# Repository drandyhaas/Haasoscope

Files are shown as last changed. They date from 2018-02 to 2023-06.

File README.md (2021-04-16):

# Haasoscope

Docs, design, firmware, and software for the Haasoscope!
Read the guide here: https://goo.gl/1Ry1k4 

Original funding campaign: https://www.crowdsupply.com/andy-haas/haasoscope (see the "updates" tab for lots of info)
Now also for sale on eBay - just search for "Haasoscope": https://www.ebay.com/sch/i.html?_nkw=haasoscope

A changelog for the python code is here: https://docs.google.com/document/d/18tjrI03KipmFqbNIHOzAKYy1VVE9wWbefSHazbPP8Gc/edit?usp=sharing and it also has pointers to changelogs for the firmware, board, and android app.

3D printable cases are available (see the guide for info)

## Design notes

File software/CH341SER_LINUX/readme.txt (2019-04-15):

// ChangeLog 
// 1.0 - 1.1   modified to solve transmition between ch341 and ch341
// 1.1 - 1.2   Support high Linux kernel
Instructions

Note: 1.Please run followed executable programs as root privilege
      2.Current Driver support versions of linux kernel range from 2.6.25 to 3.13.x
      3.Current Driver support 32bits and 64bits linux systems

Usage:
	(load or unload linux driver of CH34x)
	//compile 
	#make
	//load ch34x chips driver
	#make load
	//unload ch34x chips driver
	#make unload

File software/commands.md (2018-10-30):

Commands are received in [serialprocessor.v](../max10_adc_firmware/serialprocessor.v) and handled [in the SOLVING case](../max10_adc_firmware/serialprocessor.v#L253). Each command has a starting `id` number. Some commands take additional arguments. Commands are passed along a multiboard chain so they are seen by all boards.

`0-9` tells the board its `ID`. The first board will get usually be sent a `0`, and then it sends a `1` to the next board, which then sends a `2` to the next, and so on. Board `0` is special since it creates the clock for all boards.

`10-19` tells the board with ID 10 less to send its event data. For instance, `10` will tell board `0` to send its data. The data will be 4 channels of fast ADC data, plus additional info if other options are enabled. Each channel is sent in order, starting with channel `0`. N samples are sent for each channel, from earliest to latest in time. Each sample is one byte (8 bits), where `0` is the highest voltage for the input (e.g. 3.75V), and `255` is the lowest (e.g. -3.75V). (It's an inverting op-amp configuration.)

`20-29` tells the board with ID 20 less that it's the last one (the highest ID). For instance, sending 21 tells board with `ID 1` that it's the last board. It needs to know this in order to ignore signals on its unconnected trigger inputs on its left-side male connector.

`30-39` tells the board with ID 30 less to be the "active" board. For instance, `31` would tell the board with `ID 1` to be active, and all other boards to the right of it to be in "passthrough". Then sending another request for some data with come from the active board, and be passed through the boards to its right. If one wanted to get the board unique max10 string from board `2`, they would send `32` followed by the command to send the unique string (142).

`100` tells all boards to "arm" their triggers, and then record a new event. Note that there is also an auto-rearm mode which will always get a new event after sending the last one (see below). If the board does not record a new event, it will continue to send the same event each time it is asked to send an event.

`101`/`102` tells boards to roll / not roll the trigger. Rolling the trigger means automatically generating a trigger every 0.2 seconds (like auto mode on a scope).

`110-119` tells boards to send the "slow ADC" data from a given pin. For instance, 110 sends the data from all boards from slow ADC input 1 (pin 6), 118 would send slow ADC data from input 8 (pin 14), etc. The data is sent as N samples (set below), and each sample is 2 bytes. The first byte is the lowest 8 bits (0-255), and the second holds the higher 4 bits (0-15). It's a 12-bit ADC. So the 12-bit value is 256 times the second byte plus the first byte.

`120` (+ 2 more bytes) is how many slow ADC samples to send. It is `256*a+b` samples, where `a` is the first byte and `b` is the second byte. For instance, `120 1 10` would send `256*1+10=266` samples.

`121` (+ 2 more bytes) is the trigger point in time (how many samples to record before the trigger). It is `256*a+b` samples, where `a` is the first byte and `b` is the second byte. Add pow(2,12) to the number (i.e. 16 to a) in order to use the current timebase in the calculation (recommended!).

`122` (+ 2 more bytes) is how many fast ADC samples to send. It is `256*a+b` samples, where `a` is the first byte and `b` is the second byte. For instance, `122 1 100` would send `256*1+100=356` samples.

`123` (+ 1 more byte) is how many fast ADC samples to skip sending after each sample sent. The byte is `2^n`, e.g. if the byte is `3`, then `2^3=8` samples are skipped.

`124` (+ 1 more byte) is the "timebase", i.e. what fraction of fast ADC samples to actually record. It is `1/2^n`, so if the byte is `3`, then `1/2^3=1/8` fast ADC samples are recorded.

`125` (+ 1 more byte) is the number of clock ticks (20ns) to wait between sending serial bytes. It is `2^n`, so if the byte is `4`, then `2^4=16` ticks are waited.

`126` (+ 1 more byte) is the channel to draw on the miniscreen, e.g. `126 3` would draw channel 3 on each board's mini-screen.

`127` (+ 1 more byte) sets the trigger threshold for the fast ADC channels.

`128` (+ 1 more byte) is the type. If the byte is `1` it's a rising edge, if it's `0` it's falling.

`129` (+ 2 more bytes) is how long a channel must be above/below the trigger threshold to fire it. It is `256*a+b samples`, where a is the first byte and b is the second byte.

`130` (+ 1 more byte) toggles whether the trigger is active for a given channel, e.g. `130 6` would toggle the trigger activity for channel 6.

`131` (+ 2 more bytes) is for talking to the SPI interface on the fast ADCs on all boards. The first byte is the 7 bit address to send to on the ADC, and the second is the byte sent to that address. See the [max19506 datasheet](https://datasheets.maximintegrated.com/en/ds/MAX19506.pdf) for info, and/or see [example commands in the python programs](https://github.com/drandyhaas/Haasoscope/blob/master/software/HaasoscopeLib.py#L250).

`132/133` will send the delaycounter / carrycounter extra data (1 byte) from the active board.

`134` (+ 1 more byte) toggles the x10 gain for a given channel, e.g. `134 6` would toggle the x10 gain for channel 6.

`135` (+ 2 more bytes) says how many 2us ticks to wait after sending each 32 bytes of serial data (serialdelaytimerwait). It is `256*a+b` ticks, where a is the first byte and b is the second byte.

`136` (+ 6 more bytes!) talks over i2c to the IO expanders and DAC on the boards. The first bytes is how many bytes of info to send (not counting address). The second byte is the i2c address to send to. The 3rd-5th bytes are the data to send. And the 6th byte is which board ID to talk to (or 200 to talk to all boards). [See the python programs for examples of commands](https://github.com/drandyhaas/Haasoscope/blob/master/software/HaasoscopeLib.py#L299).

`137` toggles whether data is sent back over the serial interface or the USB2 hat.

`138` is how many ADC samples to shift the reference wave by in order to be 90deg out of phase, for lockin calculations in the FPGA.

`139` toggles auto-rearming of the trigger. Without it, you need to send `100` to record a new event each time.

`140` (+ 1 more byte) sets the "runt" trigger threshold for the fast ADC channels.

`141` (+ 1 more byte) toggles the oversampling for a given channel, e.g. `130 4` would toggle oversampling for channel 4.

`142` tells the active board to send its unique 8-byte ID back over serial.

`143` toggles "high-res" mode for all channels.

`144` toggles whether the external trigger pin is active, for all boards.

-- Following commands require the [new firmware](../max10_adc_firmware/output_files)!

`145` (+ 1 more byte) is how many channels to send data for, from each board. For instance, `145 4` would send all 4 channels from all boards. Note that the logic analyzer data is the "5th channel" on each board, so `145 5` sends all 4 channels plus the logic analyzer data. The logic analyzer data is the same number of samples as and synchronous with the fast ADC data. It is 1 byte per sample, and each bit is 0/1 for each of the 8 logic analyzer pins being low/high.

`146` (+ 3 more bytes) requests a byte to be read from i2c (e.g. ioexpander inputs) from a given i2c address, chip address, and board.

`147` requests the firmware version byte to be sent back over serial from the currently active board.

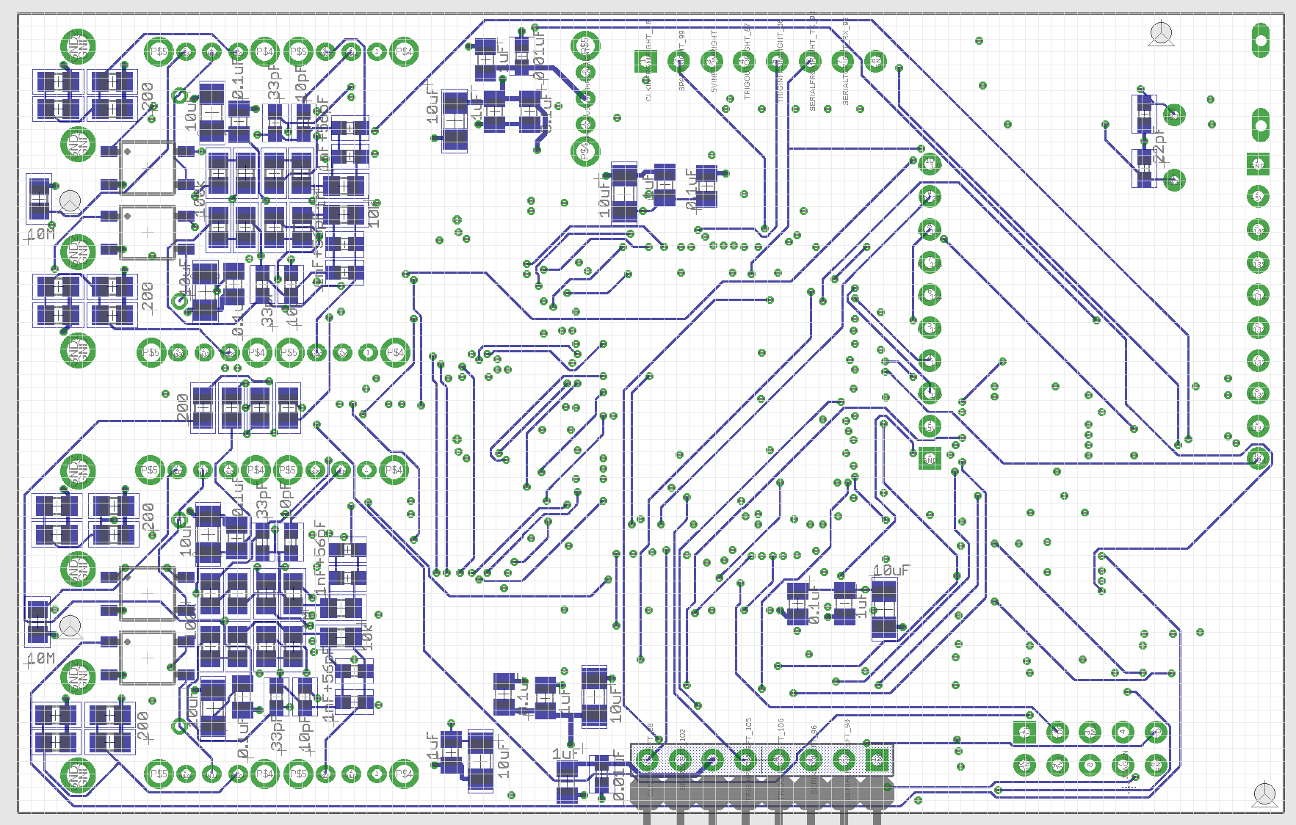
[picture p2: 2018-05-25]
eagle/max10adc_bottom_v8.png

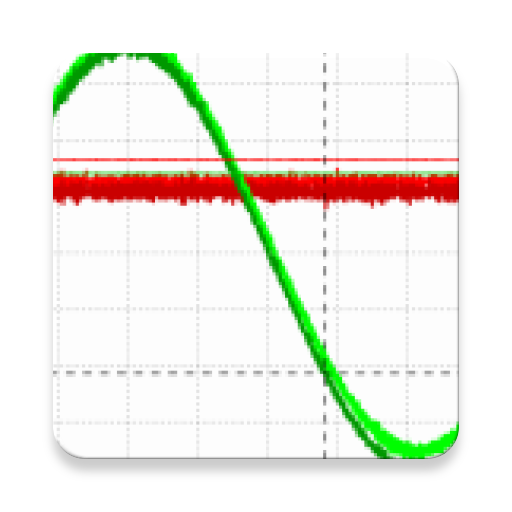
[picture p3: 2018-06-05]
android/example/src/main/ic_launcher-web.png

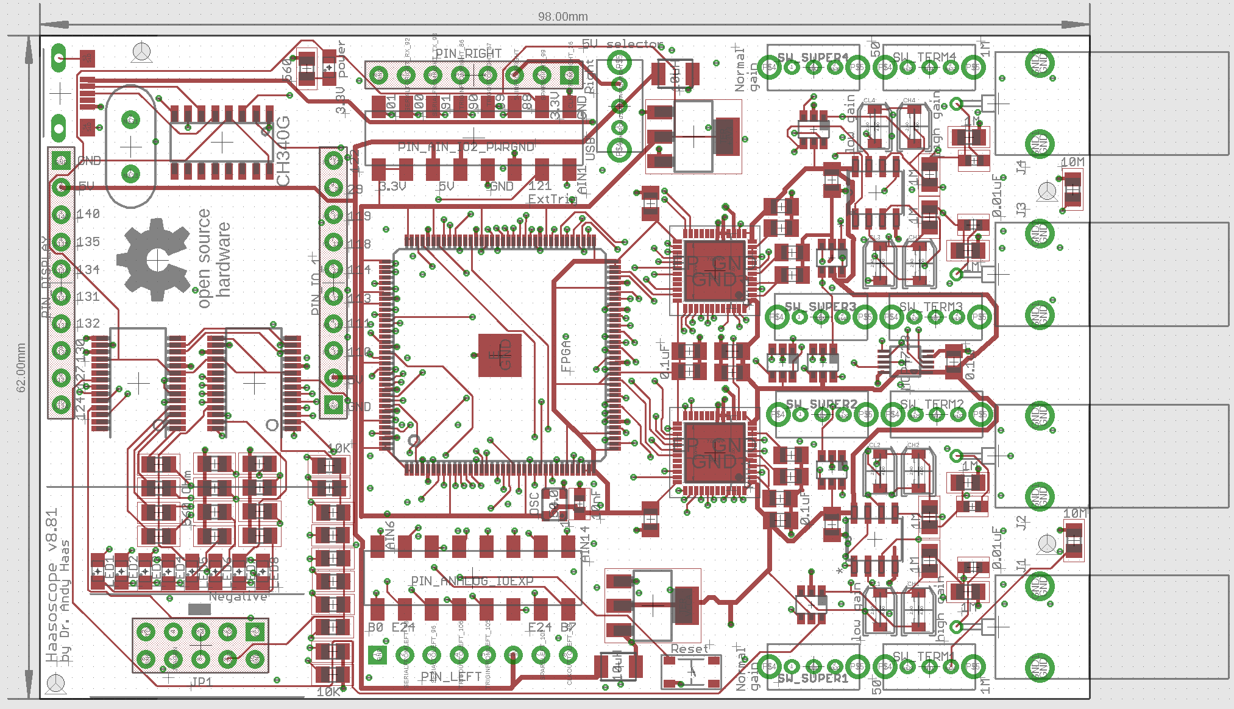
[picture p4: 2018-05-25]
eagle/max10adc_top_v8.png

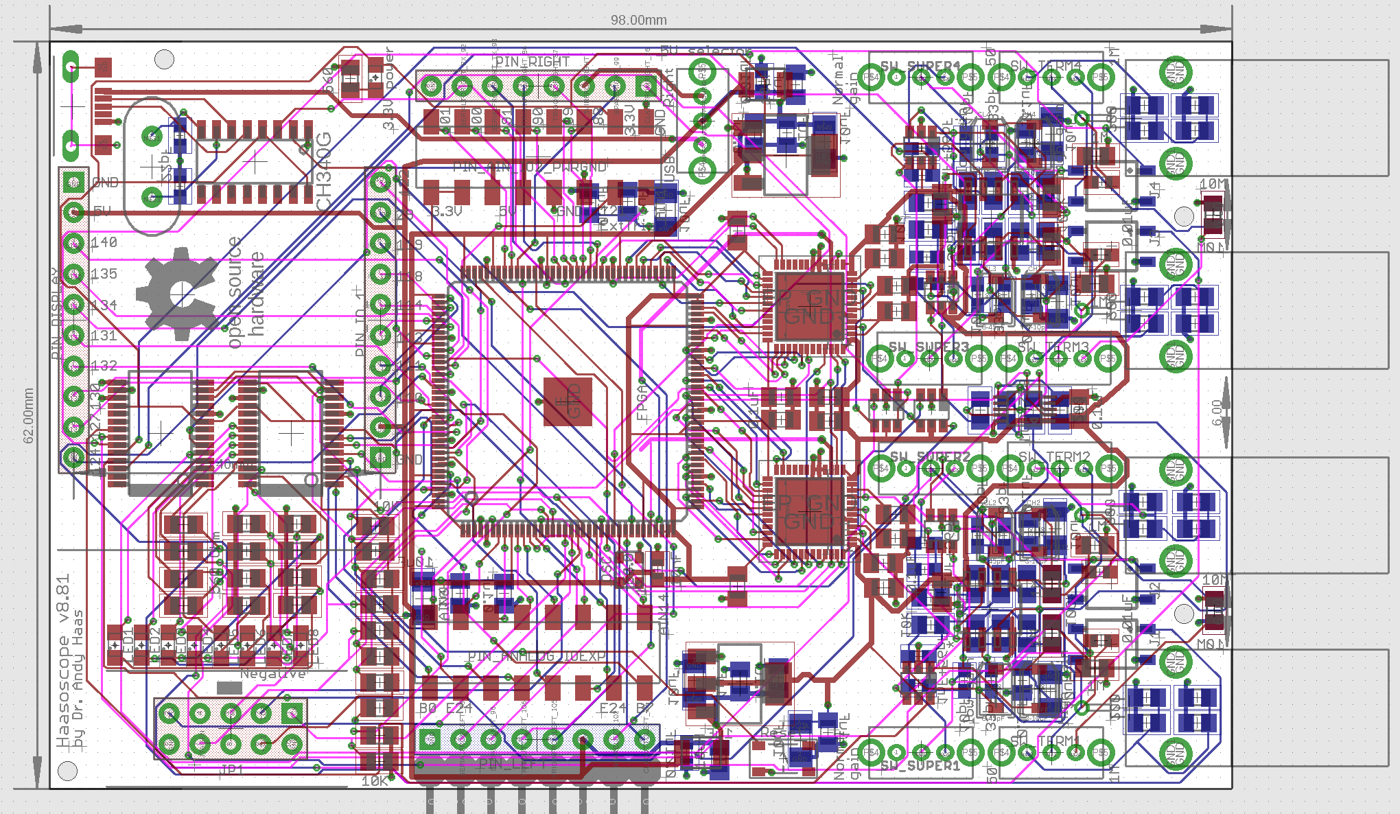
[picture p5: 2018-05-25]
eagle/max10adc_v8.png

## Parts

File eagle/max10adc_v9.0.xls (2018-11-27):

Qty | Value | Device | Package | Parts | Description | MPN | SMD | Price $ (in QTY 250 boards) | Price total (in QTY 250 boards) | Link
1 | 10M08SAE144 | 10M08SAE144 | EQFP144 | FPGA | FPGA | 10M08SAE144C8G | Yes | $16.99 | $16.99 | https://octopart.com/search?q=10M08SAE144C8G&start=0
2 | MAX19506 | MAX19506 | TQFP-48 | IC1, IC2 | analog-to-digital converter | MAX19506ETM+ | Yes | $6.77 | $13.54 | https://www.mouser.com/ProductDetail/Maxim-Integrated/MAX19506ETM%2b?qs=sGAEpiMZZMvTvDTV69d2QhUo9pNzAfXNT3AANbfnPJ4%3d
2 | MAX4416ESA | MAX4416ESA | M08A | U1, U2 | op amp | MAX4416ESA | Yes | $2.29 | $4.58 | https://www.mouser.com/ProductDetail/Maxim-Integrated/MAX4416ESA%2b?qs=sGAEpiMZZMsko7UDAsUSIQKhiCsYDWs9zfYsCt0hbUU%3d
4 | AQY21SOP | AQY21SOP | SOP04 | K1, K2, K3, K4 | PhotoMOS Relay NAiS | AQY210SZ | Yes | $0.97 | $3.86 | https://octopart.com/search?q=AQY210SZ&start=0
9 | JS202011SCQN | JS202011SCQN | JS202011SCQN | S1, S2, S3, S4, S5, S6, S7, S8, S9 | DPDT Switch | JS202011SCQN | Yes | $0.25 | $2.29 | https://octopart.com/search?q=JS202011SCQN&start=0
4 | MOLEX_BNC_73100-0105 | MOLEX_BNC_73100-0105 | MOLEX-BNC-73100-0105 | J1, J2, J3, J4 | CONN BNC JACK R/A 50 OHM PCB | 73100-0105 | No | $0.57 | $2.28 | https://www.ttiinc.com/content/ttiinc/en/apps/part-detail.html?partsNumber=73100-0105&mfgShortname=MOL&utm=tti-octo&channel=ppc&campaigns=tti-brand
2 | MCP23017SS | MCP23017SS | SSOP28 | IOEXPAND_0X20_BOT, IOEXPAND_0X24_TOP | IO expander | MCP23017-E/SS | Yes | $0.90 | $1.80 | https://octopart.com/search?q=MCP23017-E%2FSS&start=0
1 | MCP4728 | MCP4728 | MSOP10 | DAC1 | DAC | MCP4728-E/UN | Yes | $1.40 | $1.40 | https://octopart.com/search?q=MCP4728-E%2FUN&start=0
4 | 8-45pF | CAP_ADJSMD | CTZ3 | CL1, CL2, CL3, CL4 | Variable, non-polarized capacitor | TZY2K450AC01 | Yes | $0.33 | $1.31 | https://octopart.com/search?q=TZY2K450AC01&start=0
1 | ASE-50.000MHZ-ET | ASE | ASE | OSC | 3.3V CMOS SMD OSCILLATOR | ASE-50.000MHZ-ET | Yes | $1.23 | $1.23 | https://octopart.com/search?q=ASE-50.000MHZ-ET&start=0
4 | 3-10pF | CAP_ADJSMD | CTZ3 | CH1, CH2, CH3, CH4 | Variable, non-polarized capacitor | TZY2Z100AC01 | Yes | $0.25 | $0.98 | https://octopart.com/search?q=TZY2Z100AC01&start=0
2 | 15-91-2160 | PINHD-2X8SMT | 2X08_SMT | PIN_AIN_IO2_PWRGND, PIN_ANALOG_IOEXP | PIN HEADER | 15-91-2160 | Yes | $0.48 | $0.97 | https://www.ttiinc.com/content/ttiinc/en/apps/part-detail.html?partsNumber=15-91-2160&mfgShortname=MOL&utm=tti-octo&channel=ppc&campaigns=tti-brand
9 | 10uF | C-USC1206 | C1206 | CG14, COFFSETA1, COFFSETA2, COFFSETA3, COFFSETA6, CP3, CP4, CP5, CP6 | CAPACITOR, American symbol | MF-CAP-1206-10uF | Yes | $0.08 | $0.71 | https://octopart.com/search?q=C3216X5R1C106M160AA&start=0
6 | 741G3157DBVR | 741G3157DBVR | DBV_R-PDSO-G6 | GAINSW1, GAINSW2, GAINSW3, GAINSW4, OVSAMP1, OVSAMP2 | Single-Pole, Double-Throw Analog Switch | SN74LVC1G3157DBV | Yes | $0.09 | $0.55 | https://octopart.com/search?q=SN74LVC1G3157DBV&start=0
2 | LDL1117S33R | PMIC-CJT1117-3.3(SOT223) | SOT-223 | REG, REG1 | LDO regulator | LDL1117S33R | Yes | $0.18 | $0.36 | https://octopart.com/search?q=LDL1117S33R&start=0
1 | CH340G | CH340G | SOIC16 | U340G | Usb serial chip | CH340G | Yes | $0.36 | $0.36 | https://www.ebay.com/itm/50PCS-CH340G-CH340-SOP-16-IC-new-/291548393770
5 | MF-LED-0805-RED | LEDSML0805 | SML0805 | LED1, LED2, LED3, LED4, LEDPOW | LED | MF-LED-0805-RED | Yes | $0.06 | $0.32 | https://octopart.com/search?q=LTST-C171CKT&start=0
1 | MF-CON-MICROUSB-RIGHT | USB_5PIN_10118193-0001LF | 10118193-0001LF | USB1 | USB connector | MF-CON-MICROUSB-RIGHT | No | $0.29 | $0.29 | https://octopart.com/search?q=10118193-0001LF&start=0
1 | MF-SW-TACT-4.2MM | TACT_4.2MM | TACT4.2MM | SW_RESET | Reset momentary switch | MF-SW-TACT-4.2MM | Yes | $0.25 | $0.25 | https://octopart.com/search?q=PTS810%20SJK%20250%20SMTR%20LFS&start=0
25 | 0.1uF | C-EUC0805K | C0805K | C-AIN1, C-AIN2, C-AIN3, C-AIN4, C0DD1_A, C0DD2_A, C0DD2_B, C5VOPAMP1, C5VOPAMP2, CADD1_A, CADD1_B, CADD2_A, CADD2_B, CG15, CODD1_B, COFFSET, COFFSETB6, COFFSETB8, COFFSETB10, COFFSETB12, CP2, CP8, CREF1, CREF2, CV11 | CAPACITOR, European symbol | MF-CAP-0805-0.1uF | Yes | $0.01 | $0.25
1 | ABL-12.000MHZ-B2 | CRYSTALHC49US | HC49US | Y1 | Usb serial oscillator | ABL-12.000MHZ-B2 | No | $0.23 | $0.23 | https://octopart.com/search?q=ABL-12.000MHZ-B2&start=0
2 | 10uH | INDUCTOR1210 | 1210 | L1, L2 | Inductors | MF-IND-1210-10uH | Yes | $0.10 | $0.21 | https://octopart.com/search?q=LBC3225T100KR&start=0
20 | 200 | R-US_R0805 | R0805 | R50-1, R50-2, R50-3, R50-4, R50-5, R50-6, R50-7, R50-8, R50-9, R50-10, R50-11, R50-12, R50-13, R50-14, R50-15, R50-16, ROFFSET1, ROFFSET2, ROFFSET3, ROFFSET4 | RESISTOR, American symbol | MF-RES-0805-200 | Yes | $0.01 | $0.20
1 | 8p-2.54-90d | DIP-BLACK-FEMALE-HEADER-R/A(8P-2.54-90D) | H8-2.54-90D-FEMALE | PIN_RIGHT | Right side right-angle female connector | 8p-2.54-90d | No | $0.17 | $0.17 | https://www.ebay.com/itm/20PCS-2-54mm-1x8Pin-Pitch-Header-Right-Angle-Female-Single-Row-Socket-Connector/172194742559
4 | 56pF | C-USC0603 | C0603 | CIN56_1, CIN56_2, CIN56_3, CIN56_4 | CAPACITOR, American symbol | 06035A560FAT2A | Yes | $0.04 | $0.17 | https://octopart.com/search?q=06035A560FAT2A&start=0
2 | YELLOW-10P-2.54 | DIP-YELLOW-FEMALE-HEADER-VERT(10P-2.54) | H10-2.54 | PIN_DISPLAY, PIN_IO_1 | 1x10 header | YELLOW-10P-2.54 | No | $0.07 | $0.14 | https://www.ebay.com/itm/100PCS-2-54mm-1x10-Single-Row-10-Pins-Header-PCB-Socket-Female/182121619399
4 | 1nF | C-USC0603 | C0603 | CIN1NF_1, CIN1NF_2, CIN1NF_3, CIN1NF_4 | CAPACITOR, American symbol | 06035A102JAT2A | Yes | $0.03 | $0.11 | https://octopart.com/search?q=06035A102JAT2A&start=0
4 | 10M | R-EU_R0805 | R0805 | RIN5, RIN6, RIN7, RIN8 | RESISTOR, European symbol | CRCW080510M0FKEB | Yes | $0.03 | $0.10 | https://octopart.com/search?q=CRCW080510M0FKEB&start=0
1 | 2x5p-2.54 | DIP-BLACK-MALE-HEADER(2X5P-2.54) | H2X5-2.54 | JP1 | JTAG connector | 2x5p-2.54 | No | $0.10 | $0.10 | https://www.ebay.com/itm/100Pcs-Dual-Row-5-X-2-Isp-Download-Jtag-I-O-Socket-DC3-10P-2-54MM-Pitch-New-I-rn/223137742292
9 | 560 | R-EU_R0805 | R0805 | ACR1, ACR2, ACR3, ACR4, RLED1, RLED2, RLED3, RLED4, RLEDPOW | RESISTOR, European symbol | MF-RES-0805-560 | Yes | $0.01 | $0.09
8 | 100k | R-EU_R0805 | R0805 | RGAIN1_1, RGAIN1_2, RGAIN1_3, RGAIN1_4, RGAIN3_1, RGAIN3_2, RGAIN3_3, RGAIN3_4 | RESISTOR, European symbol | MF-RES-0805-100k | Yes | $0.01 | $0.08
8 | 1M | R-EU_R0805 | R0805 | RGAIN2_1, RGAIN2_2, RGAIN2_3, RGAIN2_4, RGAIN4_1, RGAIN4_2, RGAIN4_3, RGAIN4_4 | RESISTOR, European symbol | MF-RES-0805-1M | Yes | $0.01 | $0.08
8 | 10K | R-EU_R0805 | R0805 | RJ2, RJ3, RJ4, RJ5, RS6, RS7, RS8, RS9 | RESISTOR, European symbol | MF-RES-0805-10K | Yes | $0.01 | $0.08
4 | 33pF | C-USC0603 | C0603 | CGAIN1_1, CGAIN1_2, CGAIN1_3, CGAIN1_4 | CAPACITOR, American symbol | 06033A330JAT2A | Yes | $0.02 | $0.08 | https://octopart.com/search?q=06033A330JAT2A&start=0
7 | 0.01uF | C-USC0603 | C0603 | C_5V_10NF, C_5V_10NF1, C_AC1, C_AC2, C_AC3, C_AC4, C_OSC | CAPACITOR, American symbol | MF-CAP-0603-0.01uF | Yes | $0.01 | $0.07
7 | 1uF | C-EUC0805K | C0805K | CG13, CP1, CP7, CP9, CP10, CP11, CV12 | CAPACITOR, European symbol | MF-CAP-0805-1uF | Yes | $0.01 | $0.07
4 | 1.1M | R-EU_R0805 | R0805 | RIN1, RIN2, RIN3, RIN4 | RESISTOR, European symbol | CRCW08051M10FKEA | Yes | $0.01 | $0.05 | https://octopart.com/search?q=CRCW08051M10FKEA&start=0
4 | 11K | R-EU_R0805 | R0805 | RIN1_11K, RIN2_11K, RIN3_11K, RIN4_11K | RESISTOR, European symbol | CRCW080511K0FKEA | Yes | $0.01 | $0.04 | https://octopart.com/search?q=CRCW080511K0FKEA&start=0
4 | 10pF | C-USC0603 | C0603 | CIN5_1, CIN5_2, CIN5_3, CIN5_4 | CAPACITOR, American symbol | MF-CAP-0603-10pF | Yes | $0.01 | $0.04
2 | 22pF | C-USC0603 | C0603 | C_OSC1, C_OSC2 | CAPACITOR, American symbol | MF-CAP-0603-22pF | Yes | $0.01 | $0.02
2 | 10K | R-EU_R0805 | R0805 | R_SCL, R_SDA | RESISTOR, European symbol | MF-RES-0805-10K | Yes | $0.01 | $0.02
1 | 8p-2.54-90d | DIP-BLACK-SHORT-MALE-HEADER-R/A(8P-2.54-90D) | H8-2.54-90D-MALE | PIN_LEFT | Left side right-angle male connector | 8p-2.54-90d | No | $0.02 | $0.02 | https://www.ebay.com/itm/12Pcs-2-54mm-Pitch-Single-Row-Male-90-Degree-Right-Angle-Pin-Header-Q7Y4/253139448716
193 |  |  |  |  |  |  |  |  | $56.50 | Total parts
 |  |  |  |  |  |  |  |  | $9.75 | Total minor parts

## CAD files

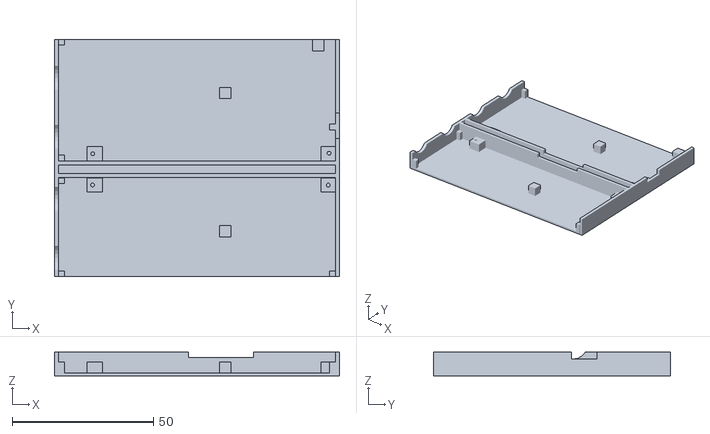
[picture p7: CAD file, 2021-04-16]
3d/Haasoscope_v9.01_case_connect.stl
101.0 x 84.0 x 8.50

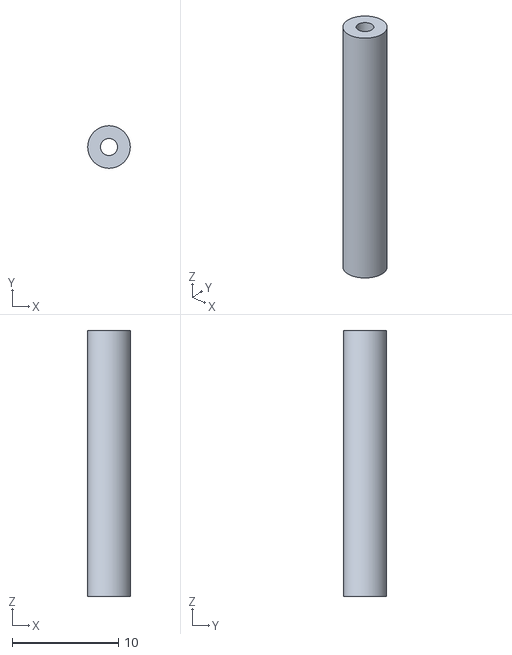
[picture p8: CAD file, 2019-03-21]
3d/customizable-cylinder_25mm.stl
4.00 x 4.00 x 25.0

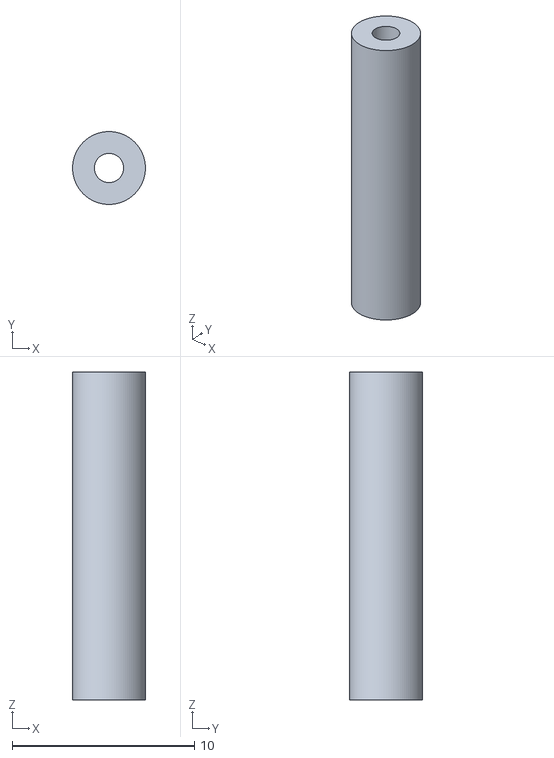
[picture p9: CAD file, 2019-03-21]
3d/customizable-cylinder_18mm.stl
4.00 x 4.00 x 18.0

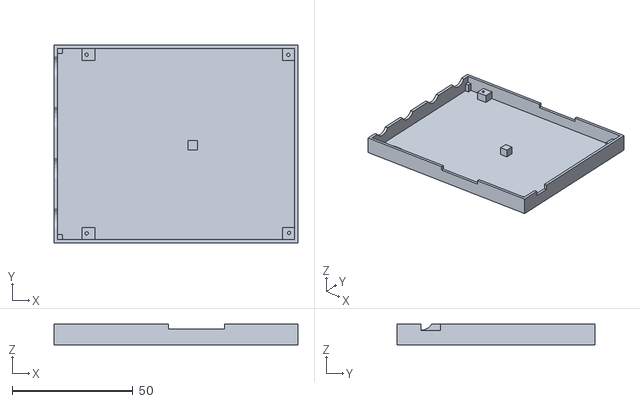
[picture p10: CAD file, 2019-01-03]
3d/Haasoscope_v9.01_case.stl
101.0 x 82.0 x 8.50

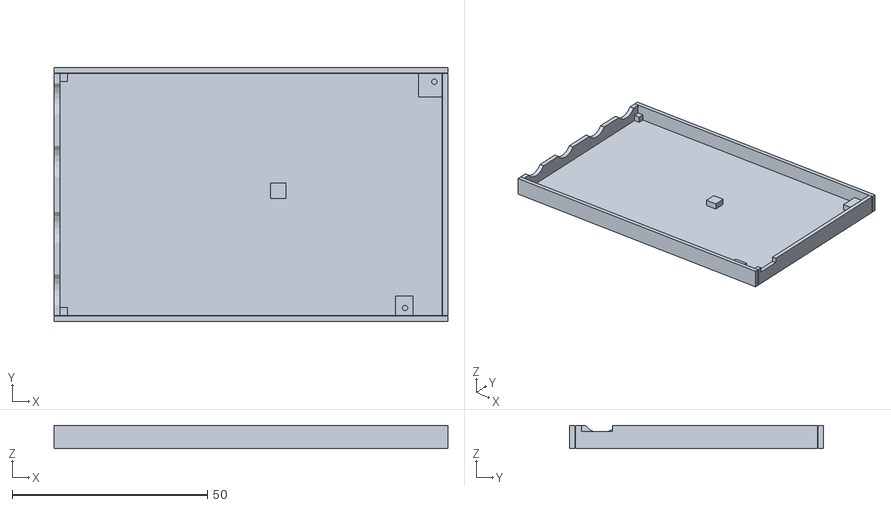
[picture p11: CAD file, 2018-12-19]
3d/Haasoscope_v8.81_case.stl
101.0 x 65.0 x 6.00

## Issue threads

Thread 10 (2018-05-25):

drandyhaas/Haasoscope #10: Probes won't compensate

g8sqh, 2018-05-25:
Cut down the probe trim tool and adjusted the pcb trimmers to get nice square waves

The probes supplied won't compensate. This is fixable thus:
- Pull the cable strain relief away from the BNC plug, and slide off the small 'box' cover
- Next to the black trimmer on the probe PCB solder on a 120 (one hundred and twenty) pF capacitor onto the two empty pads
- Refit the cover and the strain relief

This done the probes will also compensate (normal gain on PCB).

Thanks for a great product

drandyhaas, 2018-05-25:
This is true. And thanks for the tip/fix!
To be clear for others, the probe compensation (screw on the probe itself) only affects the 10x probe setting (switch on the probe itself). 
Also, the lack of compensation only affects signals below ~50 kHz, which is why I never worried too much about it. I think the reason it fails to compensate with the default cap in the probe is that I have too much (or too little?) capacitance at the BNC input. (?)

g8sqh, 2018-05-25:
I don't understand the value I needed. A normal 'real' old-fashioned scope was a fixed 30pF in parallel with 1M - they actually had trimmers on the input attenuator to keep the value constant (as well as another trimmer for compensation)

Later scopes went down to 20pF, and I think a few reached 14pF - always to reduce the loading on the circuit being measured. The screw in the probe box is directly across the BNC connector - and thus corrects for the 14-30pF range of real scopes.

HOWEVER - I had to add 120pF - not a typo - took 4 tries adding more to get it right. This tells me that the probe tip end is probably made wrong - I suspect they may have some stray capacitance across the 9M series resistor which they'd not designed for. Your BNC input would have to be around -100pF if the probe was made right - and I know of few circuits that produce a wideband negative capacitance

I'll measure the input capacitance when I have a chance - but certainly don't add capacitance to the scope PCB BNC input. I also have some known working probes on my analog scope - will try them on the Haasoscope.

Thanks for designing this PCB - I have in the past had to video my analog scope to capture rare events - digital storage is really nice to have. 

Best wishes

--David

drandyhaas, 2018-05-25:
Ahh. I think it's not the input capacitance that's the issue, actually. I played with adjusting it from 7-15 pF (it's nominally 10 pF), and not much changed. You'll also notice that the quick AC part of the response is of the correct magnitude (10x smaller than 1x), but the DC part of the response is too small. I think the input _resistance_ is too low. It's supposed to be 1 MOhm, but when it's in parallel with the input impedance of the op-amp, it drops to 600 kOhm. 

So really this 1 MOhm resistor on the board, pointed to in the pic here, should be ~10 MOhm. Seems to work OK, see below (that's using the probe at 10x setting).

[image]

[image]

g8sqh, 2018-05-25:
I've managed to open the schematic, and you're right

On normal gain the input impedance is 500K - the 1M to ground (e.g. RIN 5) in parallel with the 1M to the opamp input (e.g. RIN1). (The opamp is wired inverting, so the inverting input is a virtual ground at low frequencies. The differential impedance is 60k on the datasheet - so still 515k at higher frequencies) 

The 120pF now makes sense - we have the capacitance of about 1m of cable plus the probe trimmer + 14-30pF of scope. Probe cable is special, but I suspect 100pF/m isn't far off, probably more. 

Now make the probe operate as /19 not /10, and we need 90% more capacitance than for /10.

If you increase the RIN5,6,7,8 values to 10M then the probe will be /10.9, and should compensate as you have shown

Now I need to find some 10M resistors and take the 120pF caps out of the probes...

Many thanks - always nice when weird circuits become understood

--David

drandyhaas, 2018-05-26:
This person will sell 100 of them for 1$... with free shipping... 
https://rover.ebay.com/rover/0/0/0?mpre=https%3A%2F%2Fwww.ebay.com%2Fulk%2Fitm%2F182342653535

closed 2018-05-26 by drandyhaas

drtrigon, 2018-09-11:
I'm curious: If I would buy a Haasoscope today - would there be a 1M or a 10M resistor?

drandyhaas, 2018-09-11:
By default, it will still be the (bad) 1M resistors. At least until I spin a new batch of boards. But if it's important to you, I'd be happy to sell you one with the 10M resistors instead.

drtrigon, 2019-01-07:
Can you give an estimate when the new Board v9.0 will be ready? Then I plan to order 

1x Haasoscope
1x Oscilloscope Probes
1x A Cool Screen!
1x High-speed USB Readout Board

drandyhaas, 2019-01-07:
Hi,
Good news - it's ready!
They'll be available on eBay later today. Sounds like you want a "bundle" + "usb2 board".
Best, Andy.

drtrigon, 2019-01-08:
Will that also be available from CrowdSupply? (I don't like ebay too much)

I ebay is the only option, what's the link? Is paypal available?

drandyhaas, 2019-01-08:
https://www.ebay.com/sch/i.html?_nkw=haasoscope
It will be on CrowdSupply later this month.

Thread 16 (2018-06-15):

drandyhaas/Haasoscope #16: Oversampling doesn't seem to be working correctly

bnusbick, 2018-06-15:
When I turn on oversampling, the waveform becomes more jagged instead of smoother.  It is as if the additional samples actually took place a little before the previous samples instead of after the "normal" samples.  I am not sure, but I thought this used to work better.  Maybe this occurred when you adjusted the screen display so oversampled no longer appeared as half the frequency as normal sampling.

drandyhaas, 2018-06-15:
Hmm. Are you using the latest code? git pull?
Try turning the board totally off and then on again? I've seen the board get into a confused state where it thinks it's not oversampling but the python side does...

bnusbick, 2018-06-16:
Yes, it does appear that the board is in a confused state.  When it works correctly, the frequency appears that it has been cut in half.  When it doesn't work correctly, the frequency is not cut in half.

drandyhaas, 2018-06-16:
So sometimes it works, but then later is confused? Does it always work well right after turning it on? Again, did you check you're using the latest code please by doing a git pull?

bnusbick, 2018-06-17:
Yes, I have performed github pull to get the latest code.

Today I can't get it to work correctly with oversampling at all.
I have tried exiting the program and pulling the the usb cable and rebooting the computer multiple times.

I am using a 1 MHz square wave from a signal generator:

I see the following:
It starts up correctly displaying the signal as 1 MHz.
Then I choose to trigger on channel 0.
Then I press ''O' for oversampling.  Once I do this, the frequency cuts in half and it appears jagged.  When I press 'O' again to remove oversampling, the scope still makes the frequency appear as 500 KHz, but the jaggedness is gone.  Toggling 'O' again restores the jaggedness and the frequency remains at 500 KHz. It doesn't seem to make any difference if I remove channels 1-3 from the view or not.

drandyhaas, 2018-06-17:
Strange. Maybe try a new fresh directory with the code straight from github?
Does it work if you plug your signal into channel 1 instead of channel 0, and oversample that?
Note that the timebase should automatically change from 2 us/div (or whatever it is on, as long as it's greater than 0.5us/div) to 0.5us/div when you turn on oversampling.
See video of my test here:
https://www.dropbox.com/s/aan31bykat01khn/2018-06-17%2010.38.18.mp4?dl=0

What happens if you turn on ch.2 after you turn on oversampling? Does it look like this? It should.
[image]

bnusbick, 2018-06-18:
I looked at the video. I wish I could get the same results. I created a new github clone. I do set d.serialdelaytimerwait=600, since anything less causes the app to complain. I am also running on Lubuntu 16.04.

Here is the screenshot of what I see right after beginning the program and selecting trigger on channel 1:

[image]

when I then press 'O' to get oversampling, I see the following:
[image]

When I press 'm' and expand the time base, I see the following:
[image]

When I turn off oversampling, the jaggedness decreases as shown below:
[image]

When I turn oversampling on again and enable channel 3, I see the following (two views with differing timebases):
[image]

[image]

By the way, the cheatsheet says that 'm' is available from the matplotlib toolbar.  I don't see it, is it really there?

drandyhaas, 2018-06-18:
Ahah. It looks like the scope may be working fine.
I think there is possibly high-frequency noise present in your signal being input to the scope, which you are then seeing when using oversampling, since you are sensitive to frequencies twice as large. 
Are you using a bnc coaxial cable from the signal generator straight to the scope, as in my video? Using probes, especially with the 6" ground alligator clip cable, can pick up major noise at high frequencies.
Do you have another high bandwidth scope to try instead of the Haasoscope for comparison? You may see the same high frequency noise on that scope also.

drandyhaas, 2018-06-18:
Oh, and yes, that checkmark button on the toolbar lets you change many aspects of the lines and markers.

bnusbick, 2018-06-19:
I tried using a test frequency that was generated by another FPGA board, and I do not see the jaggedness in the waveform when oversampling.  So maybe it is due to the signal generator.
Thanks for looking into it.

closed 2018-06-20 by bnusbick

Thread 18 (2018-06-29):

drandyhaas/Haasoscope #18: Can't get single event trigger to work correctly

bnusbick, 2018-06-29:
I can't get single-event trigger to trigger when it won't trigger immediately.

For example, if I configure it as follows:
  right click to set trigger
  press 'r' to remove rolling trigger
  press 'P' to toggle single mode
If I have a continuous waveform, when I press 'p', I will see a single capture of the continuous waveform, but if there is no waveform present, I don't see a single capture when the waveform occurs.  It also doesn't trigger if I press 't' to make trigger on rising edge, and then change the voltage from 0 to +3V.

Also, when I press 'p', the console almost always displays "paused False".  Every once in a while it displays "paused True".

In summary, I can't get it to trigger when there is a single event.

If single event trigger is working for you, could you show it to me in a short video like you did with my last issue?  

Thanks.

drandyhaas, 2018-06-29:
Sure, here's a video of me using it:
https://www.dropbox.com/s/7hj29qf7isy3pa3/2018-06-29%2013.53.43.mp4?dl=0

bnusbick, 2018-06-29:
Thanks, for the quick response and video, but this is not where I am having a problem.  What I would like for you to try is:

Have no signal coming in (i.e. probe grounded) and have your trigger set to rising edge of 1.5 volts.  Then move your scope probe from ground to positive 3 volts (or so) and keep it there.  Does it trigger for you?  It doesn't for me.

Thanks.

drandyhaas, 2018-06-29:
OK, please git pull from master and try now!

bnusbick, 2018-06-30:
Thanks! It works much better now.  Sometimes it doesn't catch the transition, but most of the time it does.  My testing consists of pressing 'P' to put it in get one mode, and 't' to trigger on positive edge, then momentarily touch the probe to 3 volts and seeing if it triggers.  After it triggers, I press 'p' to arm it for another round.  I will close the issue, but you may want to try the test I tried and see if it always works for you.
Thanks.

closed 2018-06-30 by bnusbick

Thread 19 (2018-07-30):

### ISSUE TITLE
Data acquisition independent from GUI

### ISSUE THREAD

**Issue by Who8MyLunch** [drandyhaas/Haasoscope#19]
The main Python module contains all parts of the awesome oscilloscope software tool. I have a project where I'd like to sample a downconverted RF signal having a bandwidth of about 10 MHz. I don't need a GUI. I just want your Python class to be embedded in one of my own project's modules.

Do you have any thoughts about how difficult it might be to separate the GUI and drawing functions from the data acquisition and device control code?

Thanks for making this board available. I love it.

Pierre

**Comment by drandyhaas** [comment]
Hi Pierre,
There's a couple possible ways to run without a gui. The first approach will still load HaasoscopeLib.py and have access to nearly all its functionality, but without a gui. The second approach is very barebones, and does not use the HaasoscopeLib (or Draw) at all.
1)  In HaasoscopeDraw.py you can uncomment "d.domaindrawing=False" in order to not launch the gui. This still goes into the standard event loop, but exits after 50 events. You can surely find in HaasoscopeDraw.py where that happens.
While in the event loop, you can print out things in HaasoscopeDraw.py, e.g. by uncommenting lines like "print d.xydata[0][0][12], d.xydata[0][1][12] # print the x and y data, respectively, for the 13th sample on fast adc channel 0".
These are meant to serve as examples of how to access the scope draw for your own means.
2) Run software/serial_read.py instead. This does a minimal setup of the board, and then reads out one event and prints it out. You could expand upon this code to read out as many events as you like.
Good luck, and don't hesitate to write back here with further questions.
I'm glad you're enjoying the Haasoscope!
Best, Dr. Haas.

**Comment by Who8MyLunch** [comment]
@drandyhaas thanks for the replay, that's that's just what I need to know.

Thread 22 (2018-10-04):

drandyhaas/Haasoscope #22: Single Event triggering

bnusbick, 2018-10-04:
Hi Andy,
I am convinced there is a problem with single-event triggering.  My experiment consists of monitoring a switch which I set low, and then set high.  Sometimes it does not catch it going high the first time, but does on subsequent times.  I am setting it for one-event, rolling off, rising trigger, and then unpause when I want to set up for a new event.

Can you give me a clue as to where I should look to try to debug this issue?  Obviously, it is much harder to debug the hardware than software, so I would like to first somehow check to see if the events are getting to the software, but are somehow not causing a screen update.

Thanks.

drandyhaas, 2018-10-04:
If it triggers, the display will always be updated. It must not be triggering on your signal always, for some reason. What is the signal exactly? From what voltage to what voltage? Over what time interval? Does it matter what timebase you use? Where you set the trigger threshold? What about the "time over threshold" setting? (see the guide: "T followed by a number then enter: will set the number of contiguous samples above/below the trigger threshold required to fire the trigger (1 by default)" )

drandyhaas, 2018-10-04:
The samples are continuously put into a circular buffer, so the trigger is always active, except when the buffer has already triggered and is thus being read out.

bnusbick, 2018-10-05:
Hi Andy,
The attached file shows what the signal looks like.  Often times it is much dirtier, but that doesn't affect whether it catches the trigger or not.  I am monitoring it with a multimeter, and the the high voltage is 2.71 volts, and the low voltage is 0 volts.  When it doesn't trigger, the multimeter indicates that it has changed, so I am sure the voltage has changed.  It does not seem to matter what time base I use.  I have not changed the "time over threshold" setting.  I am using a clone that build that I downloaded on 10-3-2018.  The only change I made to the software was changing d.serialdelaytimerwait=600, since otherwise my computer complains about missing events.

It still fails if I change the timebase or the trigger level.  It seems to happen much less often if I set T to 2 or 5 (I was going to say never, but I did see one failure at T=2 in a couple hundred tries).  

I have included two pictures:
typical_trigger.png shows a good trigger
missed_trigger_on_up_caught_on_down.png is when missed trigger when I set switch high, but caught it when I set switch low again.

[image]

[image]

drandyhaas, 2018-10-09:
I hear you, and I'll try to reproduce this when I get a chance.

drandyhaas, 2018-10-09:
Yup, seems to work fine.

bnusbick, 2018-10-21:
Hi Andy,

I rebuilt the FPGA code with a simplified trigger as shown in the attached file.  With this file, it has never missed a high going trigger on channel 0 when in single-shot mode.  However, sometimes all the samples displayed are high, which is definitely incorrect since I always start with the signal low.  The following screenshot shows what a reasonable trigger display looks like:
[image]

The following screenshot shows all the samples high:
[image]

I think this is the reason that the submitted code has an issue, since it expects to see samples before the trigger low.

Here is the simplified oscillo.v.

[oscillo.v.txt](https://github.com/drandyhaas/Haasoscope/files/2498772/oscillo.v.txt)

drandyhaas, 2018-10-22:
Hmm. Do you have another scope you could use to debug the issue? Split your signal into the other scope and the Haasoscope, and try to get a snapshot of the signal on the other scope when it was missed by the Haasoscope. Maybe there is something pathological about the signal sometimes.

bnusbick, 2018-10-22:
Hi Dan,

I would really like to get this issue resolved.  I am quite a novice at Verilog.  Could you give me a description of the flow of getting data from the A/D chip to the PC?  From my browsing the code, I am guessing it goes somewhat as follows (I will concentrate on channel 0):

The samples come in through data_flash1 and get assigned to data_flash1_reg.
If it passes the following test:
  if (i==0) Threshold1[i] <= (data_flash1_reg>=trigthresh && data_flash1_reg<=trigthresh2);
it sets the following:
  selftrigtemp[i] = 1;
which then gets assigned to selftrig, which then gets assigned to Trigger, which then causes the following to get set:
  AcquiringAndTriggered <= 1; // Trigger? 256 more bytes and we're set
  PreOrPostAcquiring <= 1;
  wraddress_triggerpoint <= wraddress; // keep track of where the trigger happened
  state=POSTACQ;
It stays in POSTACQ until the value in samplecount is all binary 1's.  

It also seems that no matter whether it triggered or not, it is always assigning the value of data_flash1_reg to dout1.

This is where it is getting fuzzy to me.  I would guess that it should it should be storing the values from dout1 in some RAM until samplecount is all binary 1's, and then send all this data to the PC, starting with however much pretrigger samples it collected.

Since I am seeing it all high, I am guessing that the RAM is continuing to get filled after samplecount is all binary 1's, or that the pretrigger start pointer is messed up.  When I see the issue, the trigger event takes longer to complete and there is no bounce in the data, so I don't think it just a wrong starting index into the correct RAM buffer.

As you know, all the above, is in oscillo.v.  I am now starting to look at other files, but not exactly sure which are relevant.  It am guessing that I should look at WRITE1 in serialprocessor.v.

For debugging tools, I have easy access to a logic analyzer that will stream collecting 8 channels at 24 MHz for many seconds, as well as one that states that it can capture 32K 16-bit samples at 200 MHz.  I may be able to use a logic analyzer that can sample at rates much higher than 200 MHz for a couple million samples, but I would like to avoid this route.

Thanks.

drandyhaas, 2018-10-22:
Hi,
I wouldn't worry about the data flow in the firmware - it is working fine once the event is triggered. But yes, it is being stored in the FIFO buffers.
I just tried and I'm not really able to recreate your issue. I put it on the same timebase (+-256us), one-event, no rolling, and unpause for each event, and it always triggers. Things to try:
 - right click _after_ setting the time base, to set the trigger point correctly
 - then after that, do "T10<enter>" to set the number of samples (at the current timebase) that the trigger must be beyond threshold

bnusbick, 2018-10-23:
Hi Andy,
I found that it almost always correctly triggered when I added one more 0 to timercounter limit.  I then disabled the incrementing of timercounter so it will never time out, and is better still.  Maybe this is related to me having to set d.serialdelaytimerwait=600.

bnusbick, 2018-10-26:
Since disabling incrementing timercounter allows single-event ttrigger to work about 98% of the time for me, I will close this issue.

drandyhaas, 2018-10-31:
Maybe also try the latest firmware. I made some fixes to the data acquisition.

bnusbick, 2018-11-01:
Hi Andy,

This firmware works much better than before.  It catches maybe 98% of the single events.  However, a couple of times when it missed the event, and then captured my changing the switch back to low I saw the following, which is weird because I don't even have anything connected to any of the channels besides channel 0.  On a normal trace these other channels are always at 0.  Here is the weird trace after it missed catching the event:

[image]

And here is what a normal single event capture looks like:
[image]

Blake

bnusbick, 2018-11-01:
Andy,

Actually not allowing timercounter to increment performs much better for me, and it doesn't get into the state where it is displaying the wrong channels.

Blake

bnusbick, 2018-12-17:
Hi Andy,
I modified the FPGA code to bring out RxD on PIN 135 and TxD on PIN 140 to get further insight into what is happening when it fails to catch a single event.  I noticed something very interesting on the two times it failed in my limited testing.  Both times the PC started sending command 0x64 0xA while the FPGA was transmitting the acquisition data (I notice that the PC sends the 0x64 0xA command every 3 seconds while waiting for the event).

Since I am monitoring the data at the FPGA, I haven't verified that the rs232 usb chip actually sent the data to the PC, or that the PC actually got it.  I am hoping I can verify that with Wireshark.

I am also wondering if the python code clears any data that may be in the receiver buffer when it sends a new command as a recovery mechanism.  

I plan on decreasing the timeout from 3 seconds and increasing the amount of data per channel from 512 to 2048 to increase the chance of simultaneous send/receive to occur and see if missed events are always associated with this.

The only changes I made to the 12/15/18 code I cloned was modifying what came out on debug1 and debug2, and preventing timercounter from incrementing.  (I do notice that when I prevent timercounter from incrementing, the FPGA board becomes unresponsive until I reset it if I disable rolling trigger and then re-enable it again, but that I will investigate that later.)

Do you have any thoughts on what I have seen?

Thanks,

bnusbick, 2018-12-18:
Increasing the sertimeout avoids the problem.  Thanks.

closed 2018-12-18 by bnusbick

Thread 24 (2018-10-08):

drandyhaas/Haasoscope #24: Sigrok, pulseview as desktop client

luftek, 2018-10-08:
Hello,
thank you for your work.
Do you know about https://sigrok.org/ ? It is great and in active development.

drandyhaas, 2018-10-09:
Hi. Yes, I'm aware of it. I looked a bit at what would need to be done to add support for this board, and it didn't look easy. I couldn't really even figure out where to start. I think some sigrok expert would have to do it.

luftek, 2018-10-09:
Does your board/fpga have a posibility to send data over usb?
I could try to write a device driver as there are already boards supported with uart interface.

drandyhaas, 2018-10-09:
Yes, it sends data over usb with a uart protocol.
See this file for a minimal example in python of how to setup and then get data from the board:
https://github.com/drandyhaas/Haasoscope/blob/master/software/serial_read.py
Once the board is set up, you get events by sending (over uart) two bytes: 100 10.

luftek, 2018-10-09:
Does fpga have native usb protocol? Uart is probably not fast enough for highest bitrates.

drandyhaas, 2018-10-09:
The basic uart is just 1.5 Mbps, which is ~10 Hz of events (depending on num samples per event).
But there is also a USB2 "hat" available that plugs on the board and enables higher speed uart readout at about 30 Mbps (20x faster), which gets you ~hundreds of Hz!
See the guide: https://docs.google.com/document/d/1euyzCGzQo0u9APwEeior9fpyhcYWbkNxYQaV7SuFfoE/edit?usp=sharing
and look for "USB2".

luftek, 2018-10-16:
Any chance you would lend me one of this uart oscilloscopes? Would like to try and add support in sigrok project. I already have "USB hat".

drandyhaas, 2018-10-16:
Sure! I'll put the latest firmware on it, which also has the logic analyzer functionality. 
Just send me your address.

drandyhaas, 2019-01-31:
Any progress?

luftek, 2019-02-15:
What would be the procedure to get only logic analyzer data?
0. initialization as in serial_read.py (this seems to initialize more than just logic analyzer part)
1. enable logic part ('145 5') so 5th (virtual channel) on top of all analog channels
2. receive data

drandyhaas, 2019-02-16:
I don't think there's a way to get only the logic analyzer data with the current firmware.

luftek, 2019-02-16:
Ok, I see. Not a problem.
Fooling around: https://youtu.be/BYRskn1hWNk

luftek, 2019-02-16:
I can see that drawing matplots considerably limits communication refresh rate. Probably should be done in separate Thread (https://www.tutorialspoint.com/python/python_multithreading.htm).
Now that I have smaller working version, will try to add it to sigrok

luftek, 2019-02-20:
Hi Andy, I am in the process of writing HaasoscopeLib.py alternative. I will do that before sigrok implementation, to I understand the project a bit better.
Is that ok with you?
Progress will be visible on my fork. Because I am on version v8.81 of hw, will ask you to check some things.

drandyhaas, 2019-02-20:
Ok, if you like. Just let me know when you want me to have a look.

luftek, 2019-02-20:
So first commit with a lot of constrains, and probably more.
https://github.com/luftek/Haasoscope/tree/alt

luftek, 2019-03-01:
Does setting DAC affect ADC common mode voltage setting? I don't understand the direct connection.
When I run https://github.com/luftek/Haasoscope/blob/alt/software/modules/spi.py without running initialization for DACs I don't get selected voltage on C-AIN1.
[image]

drandyhaas, 2019-03-01:
Hmm. Not sure why that would be. Dac is over i2c..

luftek, 2019-03-02:
For test I initialized ADCs and 3 out of 4 DACs. I can see common voltage setting of 0,9V on 3 capacitors but not on the 4th one. Looking at the schematic I don't see the connection. Was there any change on this parts from v8,81 to v9 ?

drandyhaas, 2019-03-02:
No change to v9.
Looks like INA1 for instance comes out of the op amp, which partly takes OFFSET1 from the dac as an input.

According to the max19506 datasheet, for the adc, INA+ and INA- are connected when vcom is being used (since it's a common voltage). 

[image]

luftek, 2019-03-10:
Learning about matplotlib.
I will need some time to chew through it. Did refactor part of ..Lib.py into smaller chunks (modules).
You did great job enabling all those features.

ifishtoo, 2019-08-13:
I see this version 9 on ebay.  How is the sigrok driver coming along?

Jeffbeck67, 2019-12-15:
Hello.
In case this gives motivation, I'm also interested into a user friendly SW :)
Any chance this get on SigRok ?

drandyhaas, 2019-12-17:
I'll have a qt based gui ready to test this week!

drandyhaas, 2019-12-18:
To try out the new Qt-based gui, do
python HaasoscopeQt.py
A lot of functionality is implemented, but it's still very rough at the moment.
Please let me know what you think!

Jeffbeck67, 2019-12-19:
Hello Andy,

I've tried on Win10 and I only have a terminal that pops up and close right after.
I installed QT but did not help.

drandyhaas, 2019-12-19:
Glad the new display is working for you.
Just doing
pip install pyqtgraph
should do it. 
As for trigger, it starts up in Auto mode. This means it refreshes every 0.2 seconds even if there is no trigger. The Normal mode disables this and waits for a trigger.

Jeffbeck67, 2019-12-21:
Hello Andy,

I have some pain making the Ext Trigger working on signle shot. In fact I managed to make it working once. Otherwise I just keep displaying the curve with a trigger that I don't see where it cames from.
I use the Qt interface for ease of use. Since it look like a scope let go beyond. My remarks:
- Test doesn't display properly on a Rasp Pi. I guess you can't do much.
- The button active/disabled have a too similar color
- The Trigger part should have a led or change color once it's fired.

drandyhaas, 2019-12-21:
If you want only an ext trigger, turn off the auto trigger by clicking the button once, enable the ext trigger, turn the trigger threshold slider down to 0.

I'll work on the other things. Thanks for your feedback.!

Jeffbeck67, 2019-12-22:
Thanks, it works!
Of cours I've tried dozen of times before :)

One thing I noticed with the Qt GUI:
- If we scroll through the channels numbers and go back the " Triggering On" and Displayed box are against ticked.

In both Qt and Python Display
- Aliasing: I sample 1 MHz signal. When the time base is too slow for that frequency, a beautiful 40 kHz and this reapear at 40 Hz.

csrl, 2019-12-23:
@luftek any chance you have or still plan to make progress on sigrok support?

Jeffbeck67, 2019-12-25:
Hello all and happy holidays,

Andy, how difficult would it be to add a file capture button to the actual Qt GUI ? In order to generate a file for Excel export ?
I guess that would be an appreciable feature.

drandyhaas, 2019-12-27:
> Thanks, it works!
> Of cours I've tried dozen of times before :)
> 
> One thing I noticed with the Qt GUI:
> 
> * If we scroll through the channels numbers and go back the " Triggering On" and Displayed box are against ticked.

Not sure I understand. The "triggering on" and "displayed" properties are specific to each channel. So if you turn them off for chan 0, for instance, and then switch to chan 1, they will be back on (checked) for chan 1. But if you go back to chan 0, they should go back off.

> 
> In both Qt and Python Display
> 
> * Aliasing: I sample 1 MHz signal. When the time base is too slow for that frequency, a beautiful 40 kHz and this reapear at 40 Hz.

Yes, that is a limitation of the hardware. There are not low pass filters, other than the true bandwidth of the device, which is fixed and large. I'm not sure what to do about that.

drandyhaas, 2019-12-27:
> Hello all and happy holidays,
> 
> Andy, how difficult would it be to add a file capture button to the actual Qt GUI ? In order to generate a file for Excel export ?
> I guess that would be an appreciable feature.

OK, now you can click "Record to file" in the File menu, and the "Stop recording" to stop. Only "displayed" fast ADC channels are recorded.
I do appreciate the feedback! Please though, make a new issue in github for each issue/request, so I can keep track, close issues, etc. Thanks.
Happy holidays!

Jeffbeck67, 2019-12-28:
> OK, now you can click "Record to file" in the File menu, and the "Stop recording" to stop. Only "displayed" fast ADC channels are recorded.

Andy, you are my absolute Santa! It works fine!
just got surprized the files are 512 Samples.
Is there a way to get the sample rate as well ? Now we cannot have a horyzontal scale on the graph.

Jeffbeck67, 2019-12-28:
> Not sure I understand. The "triggering on" and "displayed" properties are specific to each channel. So if you turn them off for chan 0, for instance, and then switch to chan 1, they will be back on [...]

I confirm on the older version it did it and not on the new one.

Concerning the update Qt GUI I can't make a proper review since I had issue on my RaspPi Linux and some displays are not as nice as before.

danielkucera, 2019-12-28:
I've tested the UI and it is very usable. But I was just thinking if it wouldn't be more progressive to have the UI in browser like this guy does here: https://www.youtube.com/watch?v=aghTg4Pggv4
Not everyone can install python with Qt but everyone definitely has a browser...

zigastegu, 2020-03-23:
Sorry @drandyhaas. I kind of got stuck in March 2019.
What has changed since?

drandyhaas, 2020-03-23:
Not much really. There is a new qt gui. And less buggy firmware. 
A sigrok interface would still be really nice!

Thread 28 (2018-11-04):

drandyhaas/Haasoscope #28: Slow (3 Hz) reading of a 60 Hz signal

stalinbeltran, 2018-11-04:
**What are you trying to do?**
I have a 60 Hz signal, but the reading speed is only about 3 Hz maximum, even when disabling the display of measurements (what is supposed to give the best possible reading speed)

**What is your OS and python version?**
I use Windows 7, Python 2.7.10

**Have you installed the prerequisites?**
Yes, and the software is running.

**To Reproduce**
1)Connect a 60 Hz signal to one probe of the oscilloscope. In my case, touching the probe tip produce this signal (maybe because of the noising 60 Hz environment)
2)Check for the reading frequency. I got around 3 Hz in the best case.

**Expected behavior**
Read around 10 Hz minimum (assuming it takes 100 ms to send each data array to the computer). 

**Screenshots**
[16msSignal3HzReadings](https://drive.google.com/open?id=1qW7KdIdJxXSaJfda5y_qPFRPI3MSiBJf)

**Additional context**
I am using the micro USB cable only (not USB 2 accesory board)

Thanks for such an excellent product. Keep doing it even better.

drandyhaas, 2018-11-04:
It looks like you are getting
"getdata asked for 16384 bytes and got 7904 from board 0" type of messages. See the troubleshooting section of the guide for how to work around that problem.

drandyhaas, 2018-11-07:
Were you able to solve this? Can I close the issue?

stalinbeltran, 2018-11-07:
Yes, my fault. Sorry for the inconvenience. 
I should have noted that was the amount of data what caused the low reading frequency. I was waiting to use the USB 2 adapter to test speed and show some results, but I had no time these last days.

closed 2018-11-07 by stalinbeltran

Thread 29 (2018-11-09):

drandyhaas/Haasoscope #29: Haascope no longer recognizes by PCs

ngmacha, 2018-11-09:
I was not using my Haasoscope for several months, and now when I plug it into computer nothing even appears in Device Manager. My scope is ver.8.81 board from the Kickstarter campaign, still original firmware, and was still working OK till May. I've tried to plug it into several computers, Windows 10 as well as Windows 7, directly as well as via USB hub, changed several USB cables... Same results - nothing even appears in Device Manager!! 
Please help to identify what could be a problem - is it a faulty CH340G chip, and would it be possible to use the scope without it (connecting directly to Rx/Tx pins)? How can I check if the scope itself still working or not? It's such a good tool, what a pity if I can't use it anymore :-(

drandyhaas, 2018-11-09:
Strange. Does the power led come on?

ngmacha, 2018-11-09:
Yes, the power LED is on

drandyhaas, 2018-11-09:
Try pressing down on the ch340g chip and /or usb input when turning on the scope. It may be a loose connection?

ngmacha, 2018-11-09:
Wow, you are right, it works!! So I'll need to do some soldering... Or maybe just blowing a bit of hot gun around, what do you think?

drandyhaas, 2018-11-09:
Good. Glad we figured it out. Was it the chip or the usb port?

ngmacha, 2018-11-09:
Not sure, I pressed both :-( Will be checking in more details once I get home, my eyes are not very good without the magnifying headset...
I think I'll need to make an enclosure for it - could you advise any 3D-printed design, if you have already?

drandyhaas, 2018-11-09:
Ok. No, sorry, there's no enclosure work done so far as I know. Maybe create a new issue? And if you make progress on it share it there, thanks!

closed 2018-11-09 by drandyhaas

ngmacha, 2018-11-09:
OK, I'll try to design something and post here. Thank you again and wish you a nice weekend.

luftek, 2018-11-09:
Printable 2 part enclosure would be nice. Just though about it today. :) +1 for @ngmacha

@rdandyhaas but else, its best to design next revision of pcb around enclosure :)

ngmacha, 2018-11-09:
So the culprit is the CH340G chip, indeed - it's seated a little skewed and hence not properly soldered - you can see in the photo that pin 16 is barely touches the PCB trace:
[image]
A bit of heat-gun will fix this, I think...

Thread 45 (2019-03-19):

drandyhaas/Haasoscope #45: Can't scan JTAG chain. Error code 87

polachz, 2019-03-19:
Hallo.

I have tried to update firmware into my Haasoscope board (V 8.81) I use WIndows version and the Blaster driver provided by you to avoid the BSOD.
Then I have got this error on the command line. What can be wrong, please?

drandyhaas, 2019-03-20:
You also need to power the board through the normal usb connection (or other 5V source). The power through the jtag cable is not sufficient.

polachz, 2019-03-20:
Ok, thank you for the explanation. I'll try firmware update again today afternoon. Maybe you can improve the guide by this piece of information? I Thought about additional power, but was not sure if it si necessary ot not and if it/s not risky.

drandyhaas, 2019-03-20:
OK, clarified the guide. Thanks!

closed 2019-03-20 by drandyhaas

polachz, 2019-03-21:
I can confirm that additional power source solves the problem. Thank you for quick support!

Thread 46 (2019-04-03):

drandyhaas/Haasoscope #46: Haasoscope not communicating

anj1, 2019-04-03:
When I try to open up HaasoscopeDraw.py, I get this error:

```
Loading HaasoscopeLib.py
matplotlib backend is TkAgg
Loading HaasoscopeLib.py
matplotlib backend is TkAgg
num main ADC and max10adc bytes for all boards =  2048 and 0
rate theoretically 10.89 Hz over serial
/dev/ttyUSB0 : USB2.0-Serial : USB VID:PID=1A86:7523 LOCATION=2-1
connected serial to /dev/ttyUSB0 , timeout 3.0 seconds
got firmwareversion 0 for board 0 in 100.3 ms
```
After this all that happens is an empty graphics window pops up and nothing displays.

And the minimal serial reading script doesn't work either.

Very occasionally (e.g. once every ten times) it does work. But most of the time it gives the above error.

I'm on Linux (Ubuntu) using python 2.7.

drandyhaas, 2019-04-03:
Do you have a v8 or v9 board?
Could it be the usb cable? Or usb port on the computer?

anj1, 2019-04-03:
I've got the v9.01 board. I've tried with different USB cables and computers. All give the same issue.

anj1, 2019-04-03:
Also when I try the serial_read_versions.py script (after changing the serial port to '/dev/ttyUSB0'), I get:

```
got uniqueID  for board 0  in 1001.28 ms
got firmwareversion 0 for board 0 in 100.73 ms
```
Again, rarely it does give the correct board no, (which is 8098227110eec888), but most of the time it just gives 0 or a wrong number, like 8098227110fe7c1e.

drandyhaas, 2019-04-03:
Rarely the 50MHz oscillator can not be soldered well. Do you have a hot air soldering station? Just heat up the oscillator (right to the left of the fpga) and push it down a little onto the board better.

anj1, 2019-04-04:
I don't have a heat gun, is it possible to do the repair with a very fine tip iron?

drandyhaas, 2019-04-04:
I think it is possible. The best might be to use a little solder on the top of the device and heat up the  whole thing.

anj1, 2019-04-04:
Ok I tried that and it seems to have fixed the problem.

anj1, 2019-04-05:
After sitting for a day unused, the problem has appeared again, so I am reopening the issue.

I am not convinced that the problem is entirely due to the oscillator, as I can see the 50 MHz signal on the FPGA's input using another oscilloscope.

Furthermore, what often happens is that a few seconds after starting the GUI (with everything being normal), suddenly it reports 0 data coming from the board, and the GUI freezes.

drandyhaas, 2019-04-08:
Maybe it is still not soldered very well. If it loses clock for just a split second, it could cause some strange issue on the board.

anj1, 2019-04-09:
I don't see any reason to think it might be the oscillator; again I can see the signal very clearly and cleanly and I can't see any noise/breaks/glitches in the oscillator output. And during soldering it clearly 'slunk' itself into place indicating proper reflow.

I think it may be related to the software or firmware, as it seems to happen more often when other USB devices are plugged in. And happens rarely when there are no other USB devices. Any ideas?

drandyhaas, 2019-04-09:
I've never heard of there being such issues with software or firmware. When it works, do you see firmware version 16 reported?
Where are you located? I'm happy to send a replacement if you send back yours.

anj1, 2019-04-19:
Firmware version is 16. I'm in New Zealand. Yes I would like a replacement please.

drandyhaas, 2019-04-19:
Did you buy it on eBay? You can open a return/replacement there. 
Otherwise, please try to arrange with CrowdSupply. Please let me know if you have any problems.

closed 2019-12-06 by drandyhaas

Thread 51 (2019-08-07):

drandyhaas/Haasoscope #51: Haasoscope seems wiped after trying the FT232H USB extension board

ripzorn, 2019-08-07:
Hi 

I recently bought the extension board for the Haasoscope (I have version 9.01) on ebay (https://www.ebay.com/itm/282971875030) - It didn't include the USB2 extension cable, so I used another one - after plugging it in my Haasoscope I tried running the python script but got no response from the board. The I reattached the OLED display. But not the board seems to be wiped. I don't get a picture on the OLED display anymore and when I execute the python scripts I get no response back. The only LED that has light is the power one. The device is recognized by windows and is shown in the device manager. 
I'm using windows 10, Quartus prime version 18.1.0 and python 3.7. I had everything up and running before I installed the USB extension board. 
I have tried flashing the haasoscope with the provided pof files, but that doesn't seem to changes anything.
 
Any suggestions? 

Currently, I trying to compile the latest Max10adc firmware using my version of Quartus, but I get an error : 
" Error (18496): The Output outclk_pin in pin location 28 (pad_9453) is too close to PLL clock input pin (clock_ext_osc) in pin location 27 (pad_0)"

drandyhaas, 2019-08-07:
You tried a flashing with serial1_scope_9.0_v16_backup, and it succeeded?

ripzorn, 2019-08-07:
Just tried it and it passed. 
But still blank OLED and out response in scripts.

drandyhaas, 2019-08-07:
The compilation error you get with quartus comes from using v18.1 to compile the v8 firmware. Make sure you use the version9 branch of github for the v9 board.

drandyhaas, 2019-08-07:
It's possible some hardware issue occurred with your board. Where are you located? If you ship it back to New York, I can send you a replacement.

ripzorn, 2019-08-08:
Arh okay. The Version9 is compiling, but the end result is the same.

I'm located in Denmark (Europe) but shipping should be possible. Do you have a shipping formula or where do I look for returning the board?

drandyhaas, 2019-08-12:
You can ship to :
Andrew Haas
726 Broadway
Room 1005
New York, NY
10003

ripzorn, 2019-09-30:
> You can ship to :
> Andrew Haas
> 726 Broadway
> Room 1005
> New York, NY
> 10003
Finally got the device ship to you. It should be there within some days expect.

drandyhaas, 2019-10-14:
No package yet. Do you have a tracking number?

ripzorn, 2019-10-14:
It's a nordic postal service Postnord, and the trance and trace number is RR186092667DK.
According to them, the package was delivered on the 9th of October.

drandyhaas, 2019-10-15:
Hmmm. I don't see it at my office yet. 
It's possible it is on its way from the central University mail center to here still. It's been a 3-day weekend here in the US. 
If I don't see it today or tomorrow, I'm not sure what to do.

drandyhaas, 2019-10-15:
I just showed up!

ripzorn, 2019-10-15:
Oh Good, you had me worried about getting lost in shipping. 

I also saw that it was working the first time in plugged it in after a while (my best guess is that a capacitors needs to discharge for a day or so). But I had it running connected to the PC with the python framework running for a couple of minutes before it froze and then I couldn't get it functioning correctly - as described above.

drandyhaas, 2019-10-16:
It's been running fine all night, with the mini-display too. I don't see any issue!

ripzorn, 2019-10-16:
Well that's anoying. 
The last I remember was that it often happened when I was playing around with the time scales and voltage levels in the python frameworks. E.g., zooming out to max for a while and going back and forth. 
And that I was only using one probe on the left channel.

ripzorn, 2019-10-21:
Strange

drandyhaas, 2019-10-21:
I can send you a replacement board...
Just do it on ebay so we can use the global shipping program. I'll just lower the price to $1 or something for you.

ripzorn, 2019-10-28:
Okay, I think I would like to do that then. How do I do it via ebay then?

drandyhaas, 2019-10-30:
Send me a message about the Haasoscope in the ebay app or website. I can then send you a special offer via ebay.

ripzorn, 2019-10-31:
Hey Andrew thanks for the help and offer, however, I was under the impression that you would be sending/covering for the return shipment. If this is not the case, then I would rather make a RMA request, since the total product cost will be nearly doubled.

drandyhaas, 2019-10-31:
How much is the return shipping through ebay? Yes, I will pay for the return shipping. I can reimburse you via PayPal or something.

ripzorn, 2019-11-01:
Hey Andrew, that would be much appreciated. 
On the offer you made, I thought I saw $23 USD, but just looking at a new order now, it says US $20.81, so my guess is somewhere between that.

drandyhaas, 2019-11-02:
Ok, so make the purchase and then I will reimburse you.

ripzorn, 2019-11-29:
Should I just paste my paypal or how do you prefer?

drandyhaas, 2019-11-30:
Email me your shipping receipt and password.

logictechs, 2020-06-04:
I believe I'm having the dreaded CH340 USB to serial problems.  The device shows up fine in Windows 10 device manager.  I can run the serial_read_versions.py ok a couple times before I start getting timeout issues.  Seems to happen on my Raspberry Pi 4 also.  I also wrote a Visual Studio VB program for testing.  The same happens.  To solve the timeout issue I simply unplug the board from the USB port and return it after a couple seconds.  Can someone confirm this board really works as expected by using the USB2 interface or Bluetooth?  I was thinking of using an ESP8266 or ESP32 for TCP to serial connection.  I cannot get the HaasoscopeDraw.py to display on 2 Windows 10 machines.  On my Raspberry Pi 4 it displays but doesn't seem to be getting data correctly.  Again back to the CH340 issue.  I'm wondering if you'd consider using a FTDI chip instead of the CH340?  As long as it's genuine, it would seem to perform better.

drandyhaas, 2020-06-04:
Do you have a v8 or v9 board?
The common failures are the soldering of either the ch340 on v8 or the oscillator on v9.
You can try pushing down on the ch340 when it's failing to see if that helps, and if so you may need to touch up the soldering. Easy. 
You can tell its the oscillator because the clock signal from pin x of the oscillator will disappear or go wonky. The oscillator is a little harder to fix. If you have a hot air soldering station it's easy. Just heat it up, press down, and cool.

logictechs, 2020-06-04:
Hi Andy,

Thanks for the response and info.  I received the V9.01 kit about 2 weeks
ago now from Mouser.  I've reheated the soldering the 12Mhz crystal and the
caps near the CH340G chip.  I'll attempt reheating the osc at the Max 10
chip.  The pins of the CH340G chip seem solder well but I'll reheat them
also.

Regards,

logictechs, 2020-06-04:
After reheating the osc at the Max 10 communication seems very reliable now.  Still can't get haasoscopeDraw.py to work.  The serial_ python programs all work consistently now at least.  Thanks for the tip Andy!

drandyhaas, 2020-06-04:
Good. What's the problem with HaasoscopeDraw.py?

logictechs, 2020-06-04:
> There's also HaasoscopeQt.py now, which is better for most things, BTW.

I'll try that again when I get back to working with the Pi 4.  I'm now
fighting with my main Windows 10 machine about the CH340G driver.  It shows
up as a port but won't allow it to open.  On my bench PC it still works
ok.
Regards,

closed 2021-04-17 by drandyhaas

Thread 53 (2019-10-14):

drandyhaas/Haasoscope #53: trigger threshold and voltage offset

bnusbick, 2019-10-14:
Hi Andy,
I am converting your haasoscope to use pyqtgraph as a GUI instead of matplotlib.  I have trigger working, but am confused by some behavior I see.  If I set the voltage offset with the calibration values for my board, it triggers as I expect it to.  However, if add a negative voltage offset such as -0.5, it still triggers at the same voltage.  I it would require a voltage 0.5 volts higher. Is the trigger comparison made before the voltage offset is applied?

In case you are interested, I have attached a screenshot of my WIP pyqtgraph GUI.

Regards,
Blake
[image]

drandyhaas, 2019-10-14:
Very nice!
Hmmm. How exactly are you applying the voltage offset?

bnusbick, 2019-10-14:
Hi Andy,

I see that the lowDacLevel DC calibration value that causes the ADC reading to be 128 when I short the probe to ground is 2101.  By experiments, I see that if I add -345 per volt offset, the ADC value changes by 255 / 7 when the probe tip is still shorted to ground.  For example,  If I set my offset to -1 volt, I add 345 to 2101, and the ADC value I read is about 165.  When I say write, I call a function that is basically a copy of your setdac function in HaasoscopeLib.py with my value, which would be 2101 for no added offset, and 2446 for an offset of -1 volt.

Regards,
Blake

ngmacha, 2019-10-14:
What a nice GUI! Would it be available, can you share it, @bnusbick ?! I am not a great Python coder, but if needed I'm ready to help, at least to test on my Haasoscope!..

bnusbick, 2019-10-14:
I wouldn't mind sharing it once I get it stable.  Currently I see strange behavior way too often.  Also, even though this has nothing to do with what I do at work and I am using no company resources, I need to make sure I would not somehow be violating company rules.

ngmacha, 2019-10-16:
Please let me know when you'll be able/ready to share it! Thanks in advance - Mac Ha
> I wouldn't mind sharing it once I get it stable. Currently I see strange behavior way too often. Also, even though this has nothing to do with what I do at work and I am using no company resources, I need to make sure I would not somehow be violating company rules.

bnusbick, 2019-10-16:
Hi Andy,

Can you confirm that the offset is applied before the ADC?  If so, since this haasoscope has a range of -3.5 to 3.5 volts, is a safe way to measure signals that range from 0 to 5 volts to set the offset to -3 volts before applying the voltage that ranges from 0 to 5 volts?

As for the strange triggering when I set the offset, experiments with my pyqtgraph setup seem to show that strange behavior occurs when I send commands after sending a command to acquire data (command 100 followed by command 10) which gets no response.  For example, if I switch to and from rolling trigger when it is not receiving data because it doesn't meet the trigger, it doesn't seem to be switching.  I know it is not switching because in rolling trigger mode it should get the data whether it meets the trigger or not.  I also noticed that the trigger offset sometimes not being applied  when rolling trigger is false.

I can mostly (but not always) get around this issue by waiting (I have tried ranges from 1.6 to 3.0 seconds) the first time I send a UART or I2C command after a get data command didn't return any data.

When I looked at your verilog code many months ago, I seem to recall you had some timeout value.  I am wondering if this has something to do with it.

I am going to go as far as I can treating the FPGA  as a black box, but I think I am quickly approaching that point.  I think to understand what is really going on, I am going to need to get visibility into what the FPGA code is seeing and doing.  Many months ago I fumbled around enough to use your two FPGA diag pins as a mirror of the UART RX and TX that I could send to a logic analyzer.  I think I need to do something similar, and maybe also re-purpose your logic analyzer outputs too.  However, I had to reformat my computer since then and lost all my changes, so I am going to have to start over again from scratch.

Regards,
Blake

drandyhaas, 2019-10-16:
> Can you confirm that the offset is applied before the ADC? 

Yes, the offset is produced by the DAC, and mixed with the signal in the op-amp, then fed to the ADC.

> If so, since this haasoscope has a range of -3.5 to 3.5 volts, is a safe way to measure signals that range from 0 to 5 volts to set the offset to -3 volts before applying the voltage that ranges from 0 to 5 volts?

Yes.

> As for the strange triggering when I set the offset, experiments with my pyqtgraph setup seem to show that strange behavior occurs when I send commands after sending a command to acquire data [...]

Maybe just keep it in rolling trigger mode when sending commands.

> 
> When I looked at your verilog code many months ago, I seem to recall you had some timeout value. I am wondering if this has something to do with it.

Perhaps.
What board version (8 or 9) and firmware version are you using?

> I am going to go as far as I can treating the FPGA as a black box, but I think I am quickly approaching that point. I think to understand what is really going on, I am going to need to get [...]

OK, good luck. The firmware is really not too hard to work with once you get used to it. Start a new issue ticket if you need help with it please.

bnusbick, 2019-10-18:
ngmacha,

I will send you the code if you send me an email address.  I don't see a way to privately contact you by your github id.

ngmacha, 2019-10-18:
@bnusbick You may send to ngmacha (at) gmail (dot) com 
Thanks a lot in advance!
> ngmacha,
> 
> I will send you the code if you send me an email address. I don't see a way to privately contact you by your github id.

closed 2019-10-19 by bnusbick

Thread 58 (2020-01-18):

drandyhaas/Haasoscope #58: ADC Accuracy

Jeffbeck67, 2020-01-18:
Hello,
I've been measuring the precision of the ADCs that for 8 bits was supposed to be perfect and it seems not.
Protocol: 250 kHz triangle, 8,2Vpkpk to have full swing.  Recording 512 Samples and cropping the data to have 1 output code increase per sample.
[image]

I get up to 4 bits error. Is that possible ? 
[image]

I'm not familiar with ADC testing and my terminology is likely wrong.

drandyhaas, 2020-01-18:
First of all, that doesn't look terrible.
But how many bits is your function generator? 
Also, you could try smaller voltage swing, or slower sleep, to see if that changes things.

Jeffbeck67, 2020-01-19:
Usual question of test devices vs DUT. Frankly I don't know. It's given for 12 bit.
Below a 40 us ramp that is RC filtered. significantly better. 
that was a good lesson, I did not expect a 8 bit ADC to be so tricky to test.
[image]

closed 2020-01-19 by Jeffbeck67

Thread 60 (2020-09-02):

drandyhaas/Haasoscope #60: Worked once, and then never responds again

merckhung, 2020-09-02:
**What are you trying to do?**
I just received the board today. I see the board worked (connected ch0 only) twice or so (after reconnecting USB cable for a several times), and then on a occasion I saw the QT frond-end plots lots of noises of all 4 channels. After that, I never get the board to work again. Is there a way to troubleshoot this problem? Thank you.

**What is your OS and python version?**
Ubuntu Linux

Loading HaasoscopeLib.py
('Linux', 'lnx', '5.4.0-45-generic', '#49-Ubuntu SMP Wed Aug 26 13:38:52 UTC 2020', 'x86_64')
matplotlib backend is TkAgg
Loading HaasoscopeLib.py
('Linux', 'lnx', '5.4.0-45-generic', '#49-Ubuntu SMP Wed Aug 26 13:38:52 UTC 2020', 'x86_64')
matplotlib backend is TkAgg
num main ADC and max10adc bytes for all boards =  2048 and 0
rate theoretically 35.95 Hz over serial
/dev/ttyUSB0 : USB2.0-Serial : USB VID:PID=1A86:7523 LOCATION=1-4
connected serial to /dev/ttyUSB0 , timeout 3.0 seconds
got firmwareversion 0 for board 0 in 100.4 ms
minimum firmwareversion of all boards is 0
rolling trigger
num samples is 512
send increment is 0
do highres is True
trigger time over/under thresh now 1 and usedownsamplefortriggertot is True
serialdelaytimerwait is 100
tell SPI setup: 131  8 0
tell SPI setup: 131  6 16
tell SPI setup: 131  4 36
tell SPI setup: 131  5 36
tell SPI setup: 131  1 0
usb2 connection not available
getID asked for 8 bytes and got 0 from board 0
current directory is /home/merck/Code/Haasoscope/software
failed to get board ID for board 0
getdata asked for 2048 bytes and got 0 from board 0
don't have channel 0 on board 0
getdata asked for 2048 bytes and got 0 from board 0
don't have channel 0 on board 0
getdata asked for 2048 bytes and got 0 from board 0
don't have channel 0 on board 0
getdata asked for 2048 bytes and got 0 from board 0
don't have channel 0 on board 0
getdata asked for 2048 bytes and got 0 from board 0
don't have channel 0 on board 0
getdata asked for 2048 bytes and got 0 from board 0
don't have channel 0 on board 0
getdata asked for 2048 bytes and got 0 from board 0
don't have channel 0 on board 0
getdata asked for 2048 bytes and got 0 from board 0
don't have channel 0 on board 0
getdata asked for 2048 bytes and got 0 from board 0
don't have channel 0 on board 0
getdata asked for 2048 bytes and got 0 from board 0
don't have channel 0 on board 0
getdata asked for 2048 bytes and got 0 from board 0
don't have channel 0 on board 0
getdata asked for 2048 bytes and got 0 from board 0
don't have channel 0 on board 0
getdata asked for 2048 bytes and got 0 from board 0
don't have channel 0 on board 0
getdata asked for 2048 bytes and got 0 from board 0
don't have channel 0 on board 0
getdata asked for 2048 bytes and got 0 from board 0
don't have channel 0 on board 0
getdata asked for 2048 bytes and got 0 from board 0
don't have channel 0 on board 0
getdata asked for 2048 bytes and got 0 from board 0
don't have channel 0 on board 0
getdata asked for 2048 bytes and got 0 from board 0
don't have channel 0 on board 0
getdata asked for 2048 bytes and got 0 from board 0
[... 138 lines cut ...]
getdata asked for 2048 bytes and got 0 from board 0
don't have channel 0 on board 0
getdata asked for 2048 bytes and got 0 from board 0
don't have channel 0 on board 0
getdata asked for 2048 bytes and got 0 from board 0
don't have channel 0 on board 0
getdata asked for 2048 bytes and got 0 from board 0
don't have channel 0 on board 0
getdata asked for 2048 bytes and got 0 from board 0
don't have channel 0 on board 0
getdata asked for 2048 bytes and got 0 from board 0
don't have channel 0 on board 0
getdata asked for 2048 bytes and got 0 from board 0
don't have channel 0 on board 0
getdata asked for 2048 bytes and got 0 from board 0
don't have channel 0 on board 0
getdata asked for 2048 bytes and got 0 from board 0
don't have channel 0 on board 0
getdata asked for 2048 bytes and got 0 from board 0
don't have channel 0 on board 0
getdata asked for 2048 bytes and got 0 from board 0
don't have channel 0 on board 0
serial com failed!
failed to talk to board when cleaning up!
bye bye!

merckhung, 2020-09-02:
[image]

drandyhaas, 2020-09-02:
Sorry for the trouble.
A few others have had issues with the soldering of the 50 MHz oscillator on v9 of the board. It's the little square metal package just at the bottom left of the fpga. If you have a hot air soldering tool, try reflowing it. Or use a normal solder iron and heat it up and try to reflow it. Can you try?

merckhung, 2020-09-02:
Appreciate your helps. It works with no problem now.

Loading HaasoscopeLib.py
('Linux', 'lnx', '5.4.0-45-generic', '#49-Ubuntu SMP Wed Aug 26 13:38:52 UTC 2020', 'x86_64')
('matplotlib backend is', 'TkAgg')
Loading HaasoscopeLib.py
('Linux', 'lnx', '5.4.0-45-generic', '#49-Ubuntu SMP Wed Aug 26 13:38:52 UTC 2020', 'x86_64')
('matplotlib backend is', 'TkAgg')
('num main ADC and max10adc bytes for all boards = ', 2048, 'and', 0)
('rate theoretically', 35.95, 'Hz over serial')
('/dev/ttyUSB0', ':', 'USB2.0-Serial', ':', 'USB VID:PID=1A86:7523 LOCATION=1-4')
('connected serial to', '/dev/ttyUSB0', ', timeout', 3.0, 'seconds')
('got firmwareversion', 15, 'for board', 0, 'in', 2.16, 'ms')
('minimum firmwareversion of all boards is', 15)
rolling trigger
('num samples is', 512)
('123 send increment is', 0)
('143 do highres is', True)
('129 trigger time over/under thresh now', 1, 'and usedownsamplefortriggertot is', True)
('serialdelaytimerwait is', 100)
('tell SPI setup: 131 ', 8, 0)
('tell SPI setup: 131 ', 6, 16)
('tell SPI setup: 131 ', 4, 36)
('tell SPI setup: 131 ', 5, 36)
('tell SPI setup: 131 ', 1, 0)
usb2 connection not available
('got uniqueID', '8098227110eec444', 'for board', 0, ', len is now', 1)
('current directory is', '/home/merck/Code/Haasoscope/software')
('reading calibrations for board', 0, ', channels', 0, '-', 4)
('read', 'calib/calib_8098227110eec444.json.txt')
('calib was written using firmware version', 15)
('theboard:', 0, ' num_board:', 1, ' chan:', 0, ' num_chan_per_board:', 4)
('theboard:', 0, ' num_board:', 1, ' chan:', 1, ' num_chan_per_board:', 4)
('theboard:', 0, ' num_board:', 1, ' chan:', 2, ' num_chan_per_board:', 4)
('theboard:', 0, ' num_board:', 1, ' chan:', 3, ' num_chan_per_board:', 4)
('143 do highres is', False)
shut down adcs
bye bye!

closed 2021-04-17 by drandyhaas

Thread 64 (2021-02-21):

drandyhaas/Haasoscope #64: Running in Python 3 on Raspberry Pi

strwxq, 2021-02-21:
Was able to setup the board and run the  HaasoscopeDraw.py in Windows with Python 2,7 succesfully.
Trying to setup and run on Raspberry Pi with Python 3.7
Getting this error

Python 3.7.3 (/usr/bin/python3)
>>> %Run HaasoscopeDraw.py
Traceback (most recent call last):
  File "/home/pi/Desktop/Haasoscope-python3/software/HaasoscopeDraw.py", line 63
    if d.db: print time.time()-d.oldtime,"done with evt",nevents
                      ^
SyntaxError: invalid syntax

Before this I was not able to install PySide2, getting this error:

Looking in indexes: https://pypi.org/simple, https://www.piwheels.org/simple
Collecting PySide2
  Could not find a version that satisfies the requirement PySide2 (from versions: )
No matching distribution found for PySide2

everything else in pip3 install pyserial numpy matplotlib Qt.py scipy pyqtgraph PySide2 command seems to be there 

Not big in Linux here, just following directions so please, if anybody can explain in plain terms what I am doing worng I'd appreciate it.

drandyhaas, 2021-02-21:
Note that you have to use the python3 branch of the Haasoscope git repo...

strwxq, 2021-02-21:
The folder where all the software resided is called Haasoscope-python3 so I assume I am using the python 3 version of the code

drandyhaas, 2021-02-21:
You would have had to checkout the python3 branch. What does
git status
say?

strwxq, 2021-02-21:
I downloaded the zip file and placed the folder on desktop. Did not use git command.

drandyhaas, 2021-02-21:
Ah, OK.
But you're supposed to run 
python HaasoscopeQt.py

strwxq, 2021-02-21:
Just ran it and here's what I am getting
It seems like something is not right with numpy 
I went back and ran sudo apt-get install libatlas-base-dev
The error seems to be the same before and after

 %Run HaasoscopeQt.py
Traceback (most recent call last):
  File "/home/pi/.local/lib/python3.7/site-packages/numpy/core/__init__.py", line 22, in <module>
    from . import multiarray
  File "/home/pi/.local/lib/python3.7/site-packages/numpy/core/multiarray.py", line 12, in <module>
    from . import overrides
  File "/home/pi/.local/lib/python3.7/site-packages/numpy/core/overrides.py", line 7, in <module>
    from numpy.core._multiarray_umath import (
ImportError: libf77blas.so.3: cannot open shared object file: No such file or directory

During handling of the above exception, another exception occurred:

Traceback (most recent call last):
  File "/home/pi/Desktop/Haasoscope-python3/software/HaasoscopeQt.py", line 6, in <module>
    import numpy as np
  File "/home/pi/.local/lib/python3.7/site-packages/numpy/__init__.py", line 145, in <module>
    from . import core
  File "/home/pi/.local/lib/python3.7/site-packages/numpy/core/__init__.py", line 48, in <module>
    raise ImportError(msg)
ImportError: 

IMPORTANT: PLEASE READ THIS FOR ADVICE ON HOW TO SOLVE THIS ISSUE!

Importing the numpy C-extensions failed. This error can happen for
many reasons, often due to issues with your setup or how NumPy was
installed.

We have compiled some common reasons and troubleshooting tips at:

    https://numpy.org/devdocs/user/troubleshooting-importerror.html

Please note and check the following:

  * The Python version is: Python3.7 from "/usr/bin/python3"
  * The NumPy version is: "1.20.1"

and make sure that they are the versions you expect.
Please carefully study the documentation linked above for further help.

Original error was: libf77blas.so.3: cannot open shared object file: No such file or directory

>>>

strwxq, 2021-02-21:
The NumPy version is 1.20.1

strwxq, 2021-02-21:
Sorry scratch that.
I ran the sudo apt-get install libatlas-base-dev on a different raspberry pi. I have two of them opened via remote desktop on my desktop. My bad. 
So I ran the sudo apt-get install libatlas-base-dev on the raspberry pi the haasscope board is connected to and this is what I get now from running HaasoscopeQT.py

"
Loading HaasoscopeLibQt.py
posix.uname_result(sysname='Linux', nodename='raspberrypi', release='5.4.51-v7+', version='#1333 SMP Mon Aug 10 16:45:19 BST 2020', machine='armv7l')
On a raspberry pi?
Number of arguments: 1 arguments.
Argument List: ['HaasoscopeQt.py']
num main ADC and max10adc bytes for all boards =  2048 and 0
Construction done
libEGL warning: DRI2: failed to authenticate
qt5ct: using qt5ct plugin
qt5ct: D-Bus global menu: no
rate theoretically 66.58 Hz over serial
/dev/ttyAMA0 : ttyAMA0 : 3f201000.serial
No serial COM port opened!
"

strwxq, 2021-02-21:
Sorry, scratch that too!!! 
My desk is a mess.
The Haas-scope board was connected to the wrong raspberry pi too!!!!! The HaasoscopeQT.py window has opened !!! 
Huge embarrassment here. 
Now I am confused a bit but the graphics look completely different than in Windows. Looks like it's got more options but some of the text in the right window is cutoff

strwxq, 2021-02-21:
It keeps saying this and the image is static although I have a PWM signal connected to channel 0

don't have channel 0 on board 0
getdata asked for 2048 bytes and got 735 from board 0
(131, 0, 0, 0, 0, 0, 0, 0, 0, 0)
don't have channel 0 on board 0
getdata asked for 2048 bytes and got 768 from board 0
(0, 0, 0, 0, 0, 0, 0, 0, 0, 0)
don't have channel 0 on board 0

strwxq, 2021-02-21:
This is how my screen looks like

According to the little screen it should be showing something different

[image]

drandyhaas, 2021-02-21:
The "getdata asked for 2048 bytes and got 73..." is in the faq at the end of the guide..

strwxq, 2021-02-21:
Yep, Saw that.

This is going on a raspberry pi 3 plus. I have to update the usb. Got that.
I will try now to run it on the other raspberry pi which is a 4 and it's got two blue USB's . They should be a at least USB2's

This one is running NumPy 1.16.2 and it should be running at least NumPy 1.16.5. or at least that is the message your program errors out with. I am having a problems updating to that although I ran the same commands on both raspberry pi's .  Weird.

strwxq, 2021-02-22:
Ok. 

After numerous unsuccessful attempts in removing numpy 1.16.2 via prompt commands I was able to remove it using the Add/Remove Software in the GUI. 'Wish I thought of it earlier. With it, some other packages were automatically uninstalled and to be honest I am not sure how useful they were to what I am doing, but I did it anyway. I then installed numpy 1.20 using the same GUI. 

That fixed the problem and the HaasoscopeQT.py is working now correctly, it seems.
Sorry for the confusion between the HaasoscopeQT.py and the HaasoscopeDraw.py. I wasn't paying attention. 

Again, this is a Raspberry Pi 4 and Haas-scope board is plugged in into one of the 2 blue colored USB 3's. My other Raspberry Pi 3 b+ needs an upgraded USB because the 4 onboard USB 2's aren't fast enough.   
 
This is what the Shell output is before the program starts counting and displaying events 
The line starting with "libEGL warning"  and the next two lines are displayed in red, 'not sure what that means, maybe you can clarify. 

Some of the text lines in the right pane are cutoff or look like the text is not fitting within the space allowed and that may have something to do with the warning above or the PySide2 error I was getting earlier.

*****************************************
Loading HaasoscopeLibQt.py
posix.uname_result(sysname='Linux', nodename='raspberrypi', release='5.4.51-v7l+', version='#1333 SMP Mon Aug 10 16:51:40 BST 2020', machine='armv7l')
On a raspberry pi?
Number of arguments: 1 arguments.
Argument List: ['HaasoscopeQt.py']
num main ADC and max10adc bytes for all boards =  2048 and 0
Construction done
**_libEGL warning: DRI2: failed to authenticate
qt5ct: using qt5ct plugin
qt5ct: D-Bus global menu: no_**
rate theoretically 66.58 Hz over serial
/dev/ttyUSB0 : USB2.0-Serial : USB VID:PID=1A86:7523 LOCATION=1-1.1
/dev/ttyAMA0 : ttyAMA0 : fe201000.serial
connected serial to /dev/ttyUSB0 , timeout 3.0 seconds
got firmwareversion 16 for board 0 in 2.46 ms
minimum firmwareversion of all boards is 16
rolling trigger
num samples is 512
send increment is 0
do highres is True
trigger time over/under thresh now 1 and usedownsamplefortriggertot is True
serialdelaytimerwait is 0
tell SPI setup: 131  8 0
tell SPI setup: 131  6 16
tell SPI setup: 131  4 36
tell SPI setup: 131  5 36
tell SPI setup: 131  1 0
usb2 connection not available
got uniqueID 8098227110eebf84 for board 0 , len is now 1
current directory is /home/pi/Desktop/Haasoscope-python3/software
reading calibrations for board 0 , channels 0 - 4
No calib file found for board 0 at file calib/calib_8098227110eebf84.json.txt
100 events, 18.14 Hz
200 events, 24.31 Hz
300 events, 24.3 Hz
400 events, 24.19 Hz
****************************************

drandyhaas, 2021-02-22:
Looks good!

closed 2021-02-23 by strwxq

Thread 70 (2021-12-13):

drandyhaas/Haasoscope #70: Firmware upgrade

danielkucera, 2021-12-13:
**What are you trying to do?**
I want to upgrade firmware of the board. Is there any guide/files? I have USB Blaster.
I was getting error when running the client:
```
/dev/ttyUSB0 : USB2.0-Serial : USB VID:PID=1A86:7523 LOCATION=2-1
connected serial to /dev/ttyUSB0 , timeout 0.37014933333333333 seconds
got firmwareversion 0 for board 0 in 100.32 ms
Could not read firmware version - Exiting!
```
so I commented one line:
```
--- a/software/HaasoscopeLibQt.py
+++ b/software/HaasoscopeLibQt.py
@@ -254,7 +254,7 @@ class Haasoscope():
         print("got firmwareversion",firmwareversion,"for board",board,"in",round(tookms,2),"ms")
         if firmwareversion==0 and tookms>50:
             print("Could not read firmware version - Exiting!")
-            sys.exit(-7)
+            #sys.exit(-7)
         return firmwareversion # is 0 if not found (firmware version <5)
     
     def telltickstowait(self):
```
and it runs now:
```
Loading HaasoscopeTrigLibQt.py
Argument List: ['HaasoscopeQt.py']
num main ADC and max10adc bytes for all boards =  2048 and 0
Construction done
Warning: Ignoring XDG_SESSION_TYPE=wayland on Gnome. Use QT_QPA_PLATFORM=wayland to run on Wayland anyway.
rate theoretically 35.95 Hz over serial
/dev/ttyUSB0 : USB2.0-Serial : USB VID:PID=1A86:7523 LOCATION=2-1
connected serial to /dev/ttyUSB0 , timeout 0.37014933333333333 seconds
got firmwareversion 0 for board 0 in 100.36 ms
Could not read firmware version - Exiting!
minimum firmwareversion of all boards is 0
rolling trigger
num samples is 512
send increment is 0
do highres is True
trigger time over/under thresh now 1 and usedownsamplefortriggertot is True
serialdelaytimerwait is 100
tell SPI setup: 131  8 0
tell SPI setup: 131  6 16
tell SPI setup: 131  4 27
tell SPI setup: 131  5 27
tell SPI setup: 131  1 0
usb2 connection not available
got uniqueID 80988211106e2028 for board 0 , len is now 1
current directory is /storage/Projects/Haasoscope/software
reading calibrations for board 0 , channels 0 - 4
read calib/calib_80988211106e2028.json.txt
calib was written using unknown firmware version
```

The QT UI works now, but I would prefer to update the FW anyway.
My HW version is v8.81

**What is your OS and python version?**
Linux, Python 3.9.7

**Have you installed the prerequisites?**
Yes

drandyhaas, 2021-12-13:
Instructions for upgrading with new firmware are in the Haasoscope guide.
But new firmware for v8 boards has not been made for some time. The python3 Qt gui is only tested with v9 boards and their associated firmware.

danielkucera, 2021-12-13:
Not the best support I have to say. And I wanted to write integration for glscopeclient... Nevermind, I'll find some other hardware.

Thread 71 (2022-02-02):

drandyhaas/Haasoscope #71: Could not read firmware version - Exiting!

bradkyle, 2022-02-02:
I want to launch HaasoscopeQt.py

OS:Arch linux, python:3.10.2, conda environment

$python ./HaasoscopeQt.py
Loading HaasoscopeTrigLibQt.py
Argument List: ['./HaasoscopeQt.py']
num main ADC and max10adc bytes for all boards =  2048 and 0
Construction done
rate theoretically 35.95 Hz over serial
/dev/ttyUSB0 : USB2.0-Serial : USB VID:PID=1A86:7523 LOCATION=1-1.2.2
connected serial to /dev/ttyUSB0 , timeout 0.37014933333333333 seconds
got firmwareversion 0 for board 0 in 100.34 ms
Could not read firmware version - Exiting!

expected launch haasoscope software.

I have tried flashing latest firmware, updating libraries, changing python env, rebooting computer, resetting haasoscope, unplugging probes, rebooting haasoscope, reinstalling all libraries, changing udev rules.
I also modified the HaasoscopeLibQt.py to rule out the error: however it then throws the error that it cant connect via usb?

Could anyone please advise me how I can resolve or at least troubleshoot this?
Thanks

drandyhaas, 2022-02-02:
What hardware version of the board do you have? v8 or v9?
I assume you are running this from the master branch of the git repository? And it is up to date (git pull)?

bradkyle, 2022-02-09:
Yes:
Board harware version: v9.
Running from master branch.

drandyhaas, 2022-02-09:
You closed the issue. Did you get it to work?

bradkyle, 2022-02-11:
No, the problem persists.

bradkyle, 2022-02-11:
I've tried changing usb cables, usb ports, computers, operating systems. On occasion it launches but the cause therein is not readily verifiable.

drandyhaas, 2022-02-11:
It can also be the soldering of the 50MHz oscillator near the Fpga. Try pressing down on it. Or reflow it if you know how.

bradkyle, 2022-02-11:
Just tried this. The failure generally triggers when a secondary bnc probe is attached//signal collected. I don't know if there exists a causal link just yet.

drandyhaas, 2022-02-11:
Even if the other end of the probe is not attached to anything? That would be weird. 
I could imagine big problems if the ground clip of the attached probe is put on something with a voltage significantly different from the ground of the USB connection...

closed 2022-12-02 by drandyhaas

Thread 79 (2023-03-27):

### ISSUE TITLE
New 3d case for the Haasoscope

### ISSUE THREAD

**Issue by KevinOConnor** [drandyhaas/Haasoscope#79]
This is not an issue; it is notification of a 3d printable case that I designed for the Haasoscope.  Let me know if there is a better place to discuss topics like this.

I designed a case for the Haasoscope: https://github.com/KevinOConnor/hcase (and https://www.printables.com/model/356793-haasoscope-case ).  The haasocope board can "click" into the bottom of this case and the top of the case can also "click" into the bottom.

This case also encloses all the pins (only the bmc connectors extend from the case).  There are openings for most ports, including the usb port of the "hi speed usb module".

-Kevin

**Comment by drandyhaas** [comment]
Thanks!

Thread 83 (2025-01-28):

drandyhaas/Haasoscope #83: Strange behavior when try to increase functionality

bnusbick, 2025-01-28:
Hi,

As I mentioned I would do previously, I have  rewritten most of the FPGA and PC code for my Haasoscope, and am rather pleased with the result.

What I would like to do now is increase the voltage range that can be fed into m V9.01 Haasoscope.  I know I can use the 10x mode to increase the range, but that is too much, and thus I would get very few bits for a signal that changed from say 0-5 volts.  My idea is to use the same technique that x10 uses, namely putting a large resistor in parallel with a capacitor before the scope 1Mohm resistance.

For my initial experiments, I have added 1.330 M ohm resistance, and thus would expect the voltage measured would be 1/2.33 of the reading that would otherwise be read.  After adjusting the zero offset, my Haasocope reads 128 when I short the probe ground to tip, 0 when I apply 4 volts, and 32 when I apply 3 volts, so it appears the maximum voltage is 4 volts.  With the additional 1.33 M ohm resistance, I would expect the reading to be about 128 - (3/4) * 128 * (1/2.33) = 41.2, but it reads 72.

Also, if I short the probe ground to the end of the 1.33 M ohm connected to the probe tip, it measures 113 instead of the expected 128.

I am not much of a hardware person (but I am try to be more so), so I am not able to understand this behavior from looking at the schematic.  Could you explain why I see what I do?  If there is some additional calculation I need to perform to adjust for the addition of 1.33M ohm (or other values to get larger ranges), I could easily adjust the PC code so it would display correctly.

As a sanity check, I applied the same additional 1.33 M ohm to the tip of a probe connected to a Tektronix 2230, and the voltage I measured when applying 3 volts was 1.3 volts  (3 * 1 M ohm / 2.33 M ohm) as expected, and 0 volts when I connected the probe tip to the 1.33 M ohm additional resistance that I added to the the scope tip.

Thanks in advance for any help you can provide.

drandyhaas, 2025-01-28:
Sounds like a good project for learning!
I'm a bit unclear what you're trying to do. You want not 10x gain, but say, 3x gain? The gain is controlled by 1MOhm RGAIN2_1 and RGAIN4_1, in parallel with the 3-10pF variable cap. You would adjust those values to change the gain.

bnusbick, 2025-01-28:
I am trying to create a 2.3x gain without modifying the board.  Looking on the web, scope probes add a 9M ohm resistor between the probe tip and the 1 M ohm resistor to create 10x gain. I was hoping adding 1.3 M ohm at the probe tip, and then connecting to a gripper that I attach to this would give 2.3x gain.

bnusbick, 2025-01-29:
If I short the probe ground lead to the end of the additional 1.33 M ohm resistance I added to the probe tip, and then offset that reading to 0, I get the proper behavior, i.e. the readings are 1/2.33 of what they would be without the additional 1.33 M ohm resistance, and when I feed 9.4 volts in, the A/D converter sends 0.

closed 2025-01-30 by bnusbick

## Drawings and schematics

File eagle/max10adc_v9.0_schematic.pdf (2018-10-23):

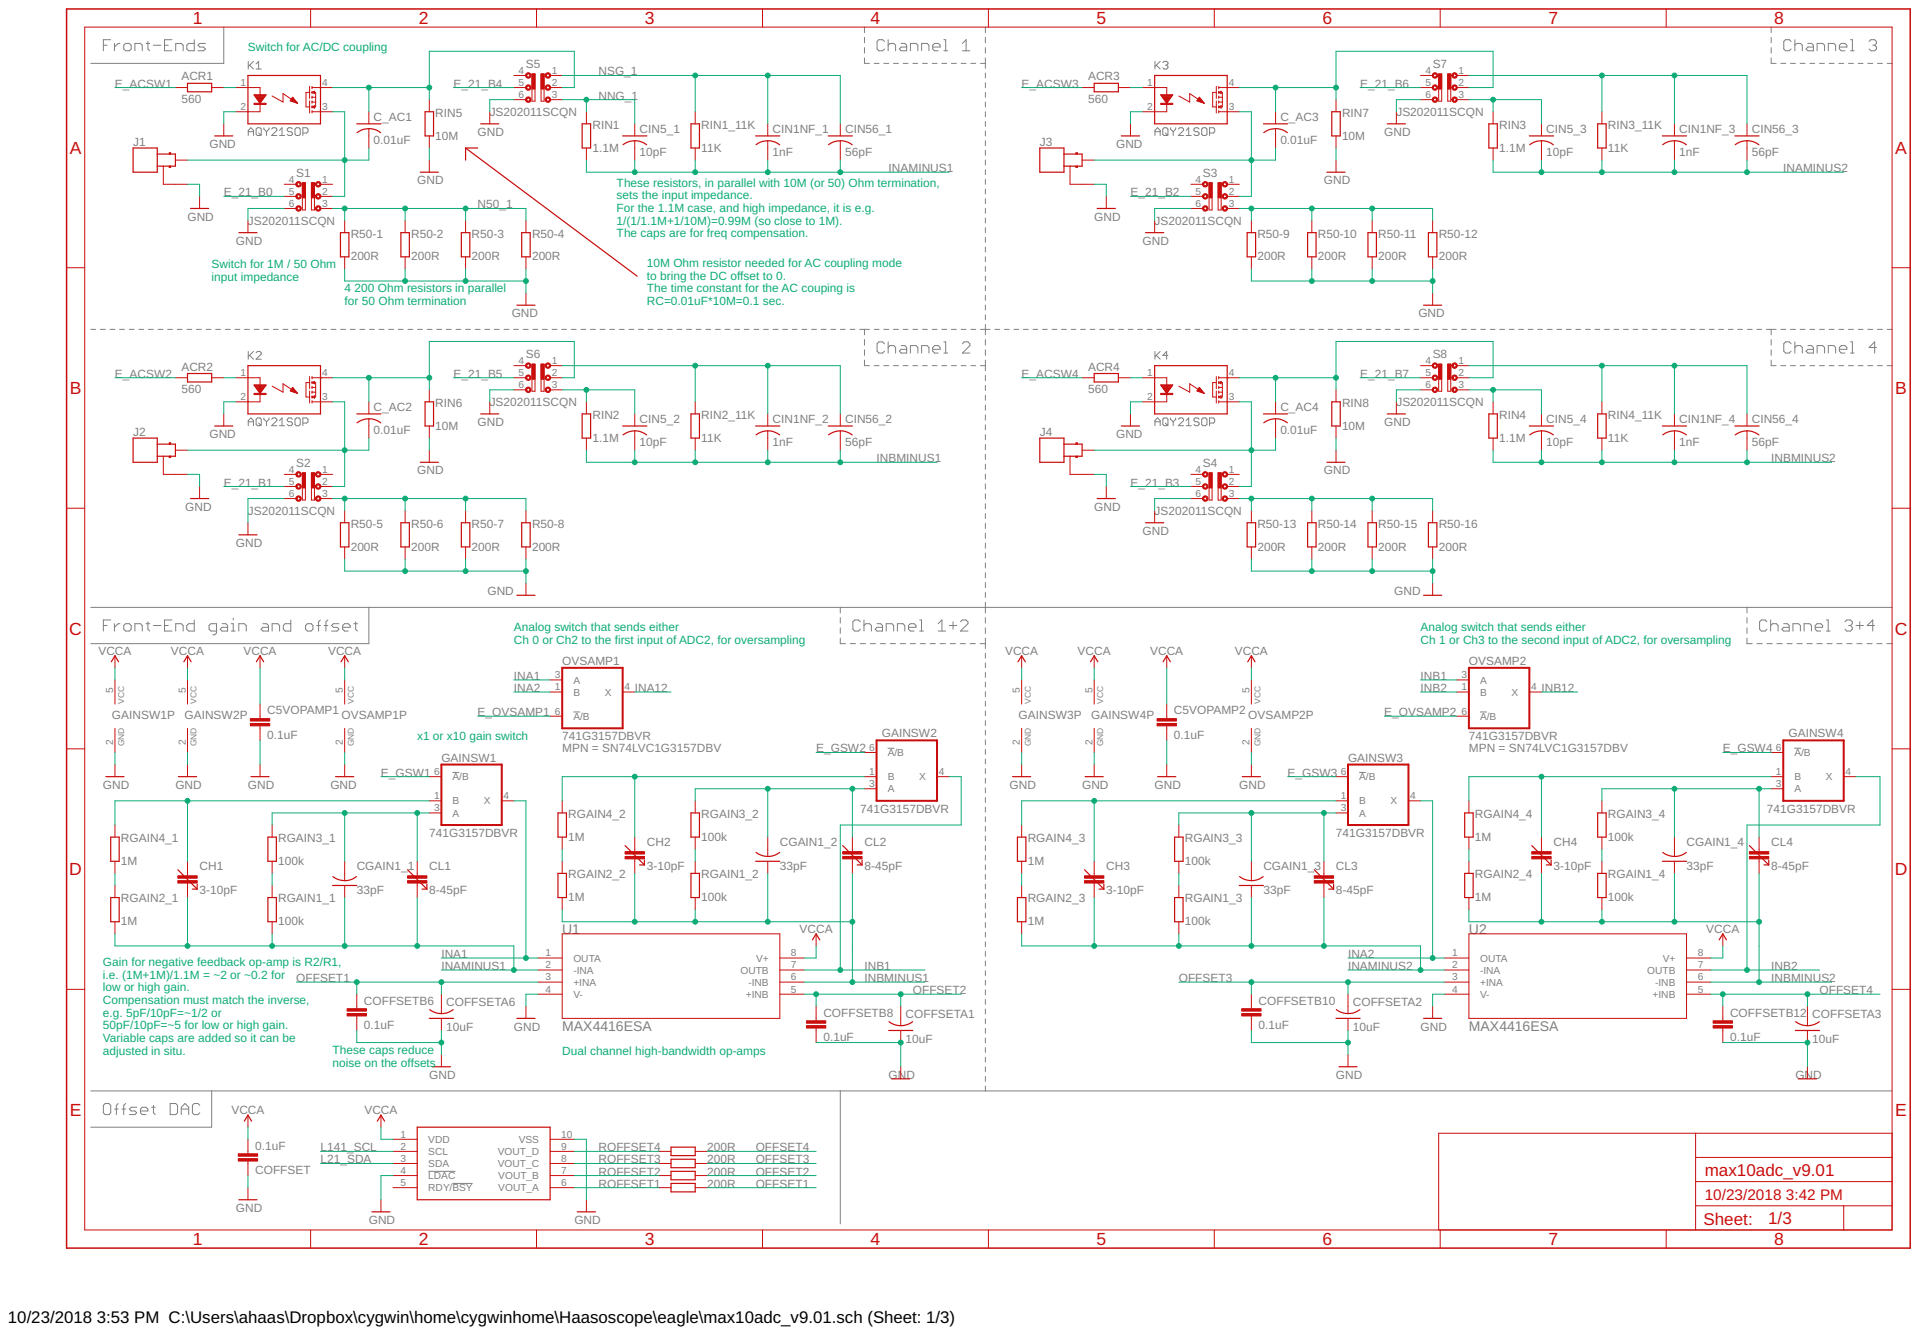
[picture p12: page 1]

Switch for AC/DC coupling

These resistors, in parallel with 10M (or 50) Ohm termination, sets the input impedance. For the 1.1M case, and high impedance, it is e.g. 1/(1/1.1M+1/10M)=0.99M (so close to 1M). The caps are for freq compensation.

10M Ohm resistor needed for AC coupling mode
to bring the DC offset to 0. The time constant for the AC couping is RC=0.01uF*10M=0.1 sec.

4 200 Ohm resistors in parallel
for 50 Ohm termination

Analog switch that sends either Ch 0 or Ch2 to the first input of ADC2, for oversampling

Analog switch that sends either Ch 1 or Ch3 to the second input of ADC2, for oversampling

Gain for negative feedback op-amp is R2/R1,
i.e. (1M+1M)/1.1M = ~2 or ~0.2 for
low or high gain. Compensation must match the inverse, e.g. 5pF/10pF=~1/2 or 50pF/10pF=~5 for low or high gain. Variable caps are added so it can be

These caps reduce
noise on the offsets

Dual channel high-bandwidth op-amps

10/23/2018 3:53 PM C:\Users\ahaas\Dropbox\cygwin\home\cygwinhome\Haasoscope\eagle\max10adc_v9.01.sch (Sheet: 1/3)

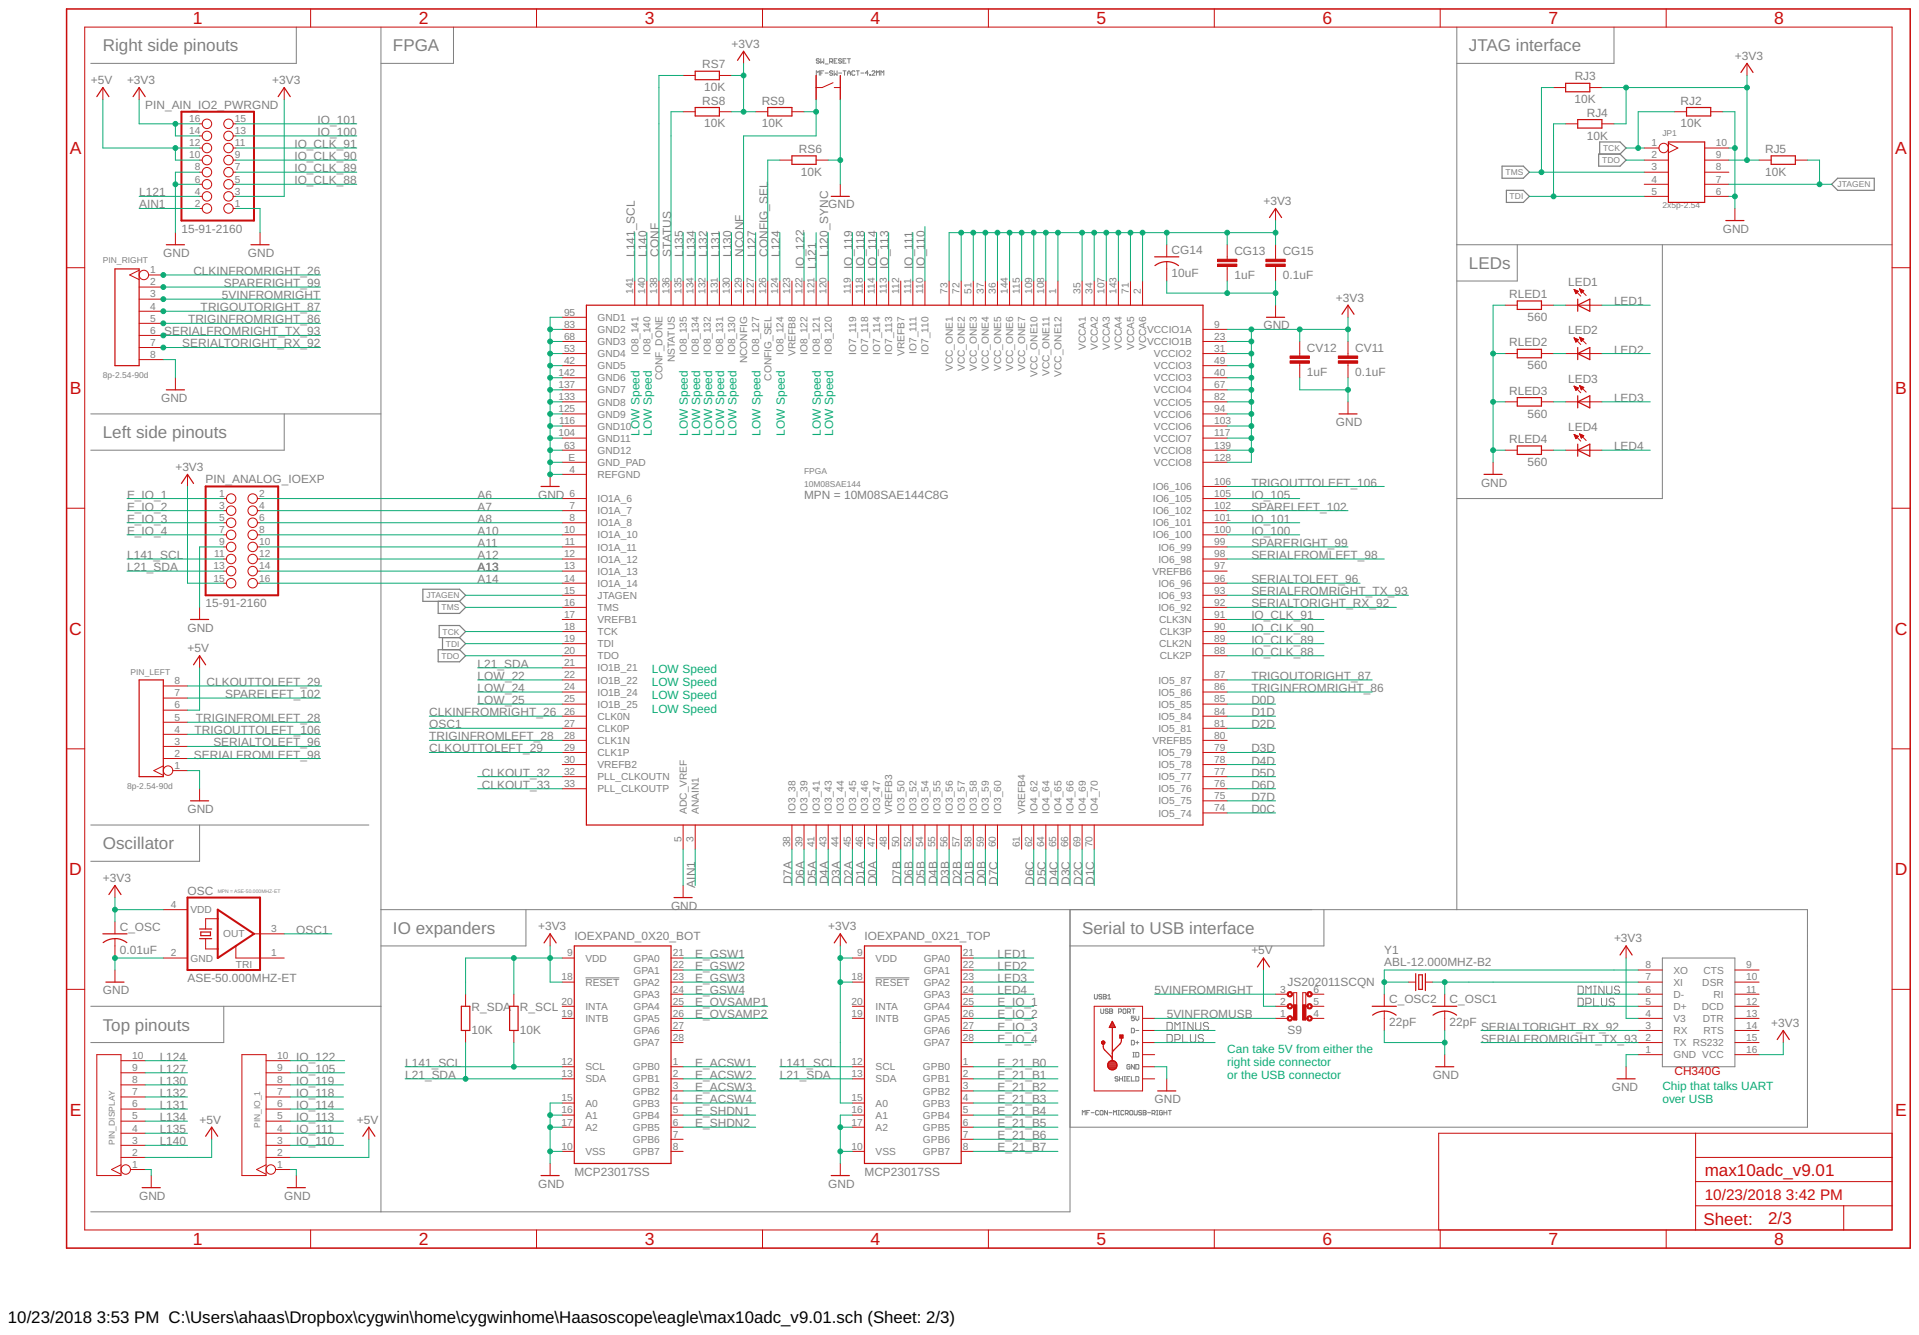
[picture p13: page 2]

1 OSC
MPN = ASE-50.000MHZ-ET ASE-50.000MHZ-ET

Can take 5V from either the

10/23/2018 3:53 PM C:\Users\ahaas\Dropbox\cygwin\home\cygwinhome\Haasoscope\eagle\max10adc_v9.01.sch (Sheet: 2/3)

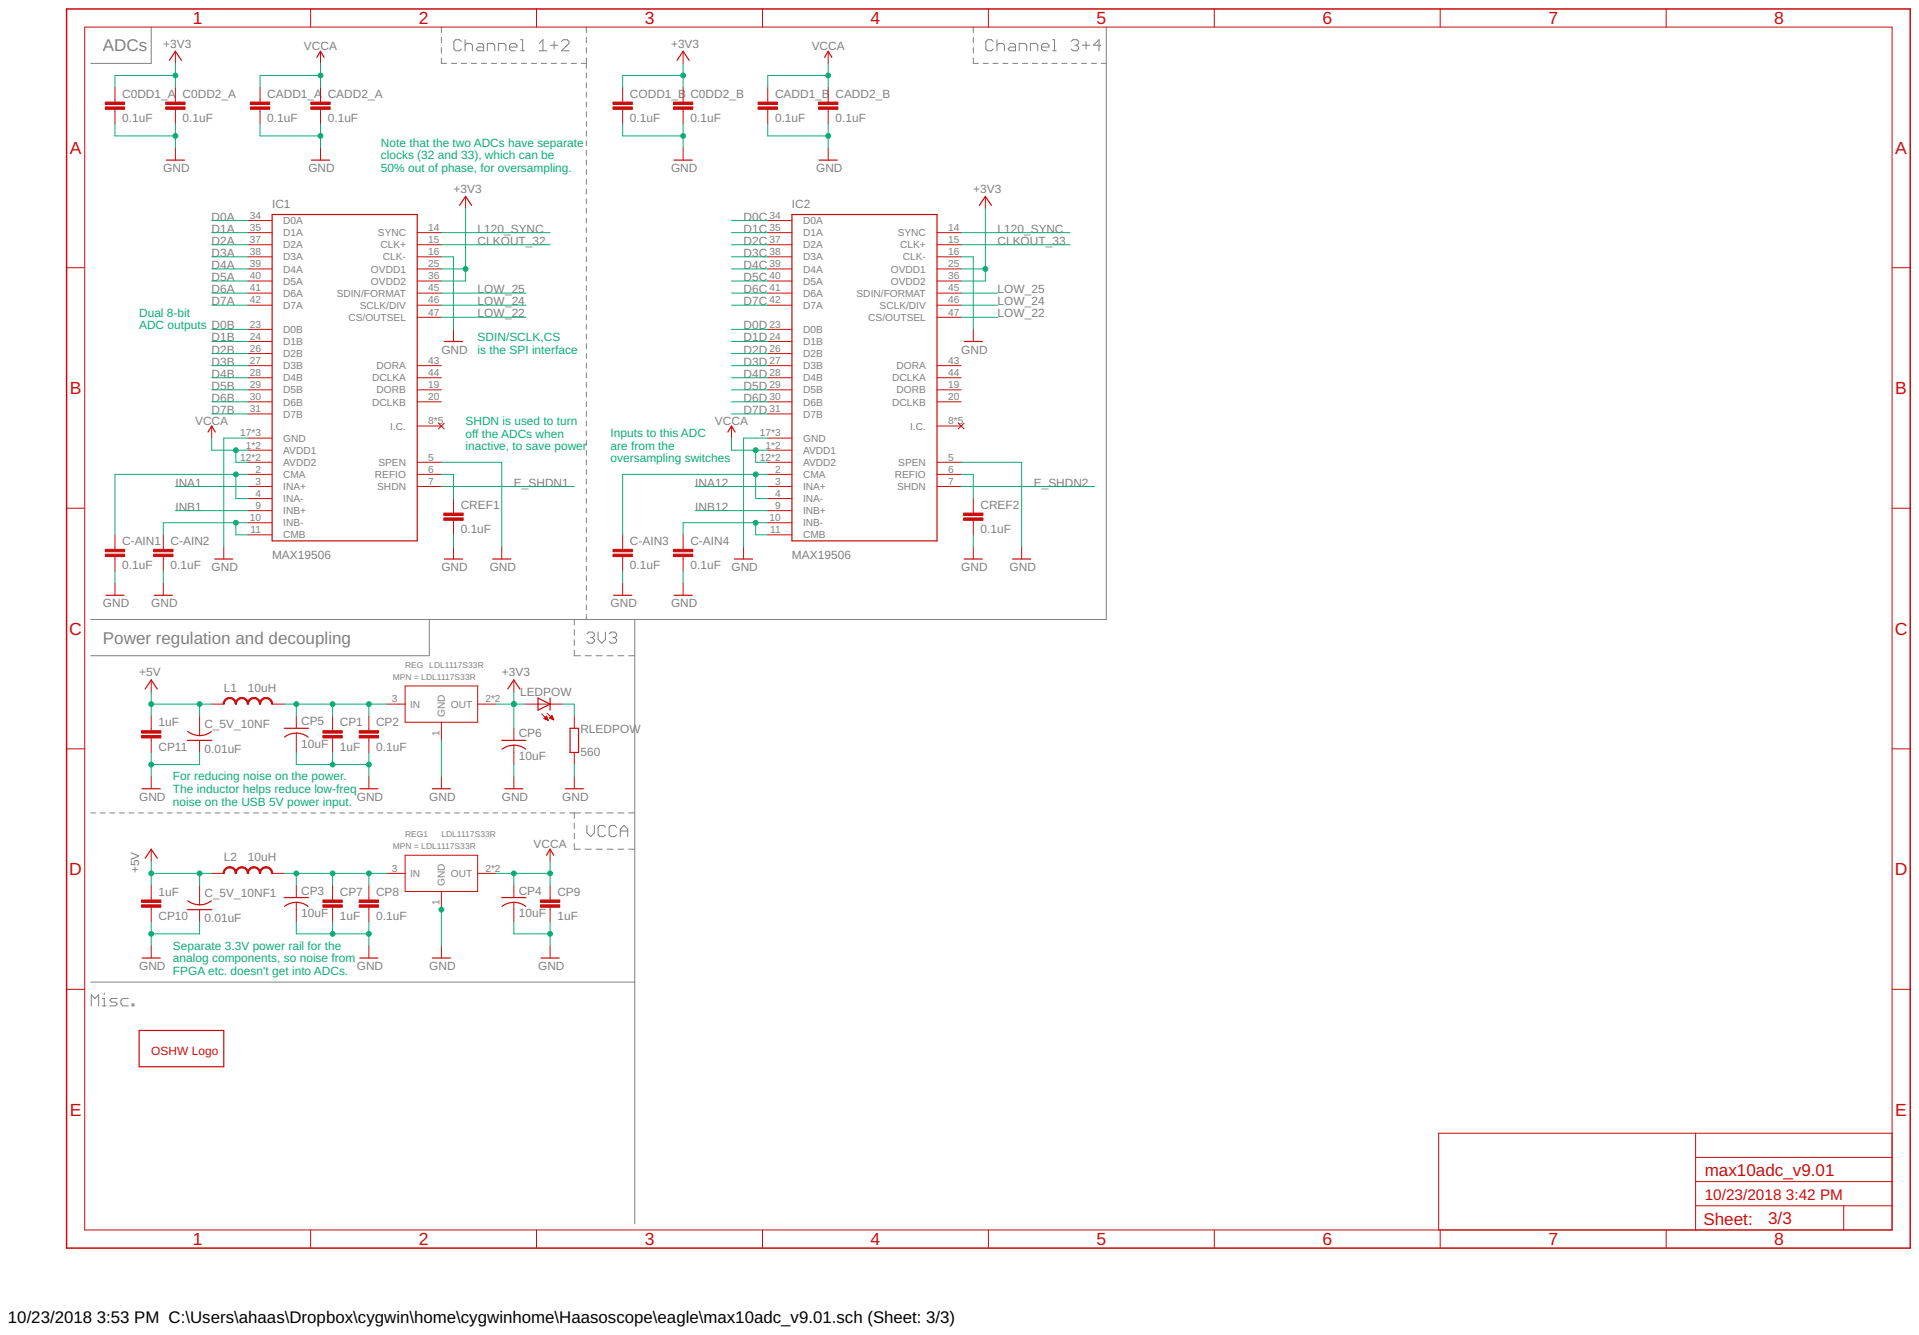
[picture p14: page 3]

Note that the two ADCs have separate
clocks (32 and 33), which can be
50% out of phase, for oversampling.

is the SPI interface Dual 8-bit
ADC outputs

SHDN is used to turn
off the ADCs when
inactive, to save power

Inputs to this ADC
are from the
oversampling switches

For reducing noise on the power. The inductor helps reduce low-freq

noise on the USB 5V power input.

Separate 3.3V power rail for the
analog components, so noise from
FPGA etc. doesn't get into ADCs.

10/23/2018 3:53 PM C:\Users\ahaas\Dropbox\cygwin\home\cygwinhome\Haasoscope\eagle\max10adc_v9.01.sch (Sheet: 3/3)

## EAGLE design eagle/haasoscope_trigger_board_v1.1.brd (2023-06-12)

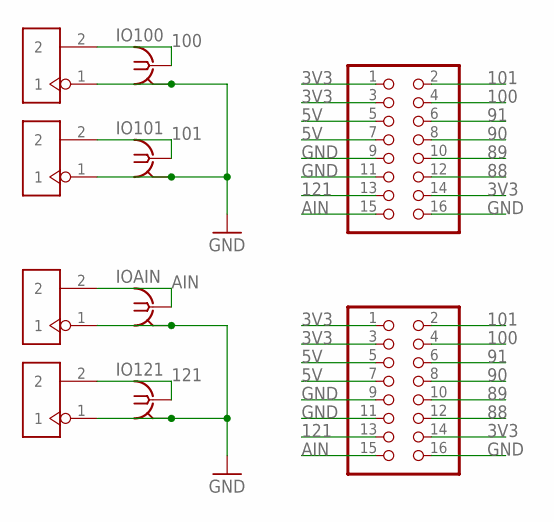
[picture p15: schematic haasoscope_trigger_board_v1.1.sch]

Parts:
IO100, IO101, IO121: BU-SMB-V
IOAIN: BU-SMB-V
J1, J2, J3, J4: 2p-2.54; H2-2.54
JP1: Jp1; 2X08
JP2: JP2; 2X08

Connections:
3V3: JP1.1, JP1.3, JP1.14, JP2.1, JP2.3, JP2.14
5V: JP1.5, JP1.7, JP2.5, JP2.7
88: JP1.12, JP2.12
89: JP1.10, JP2.10
90: JP1.8, JP2.8
91: JP1.6, JP2.6
100: IO100.1, J1.2, JP1.4, JP2.4
101: IO101.1, J2.2, JP1.2, JP2.2
121: IO121.1, J4.2, JP1.13, JP2.13
AIN: IOAIN.1, J3.2, JP1.15, JP2.15
GND: IO100.2, IO100.3 (2), IO100.4 (2), IO100.5 (2), IO101.2, IO101.3 (2), IO101.4 (2), IO101.5 (2), IO121.2, IO121.3 (2), IO121.4 (2), IO121.5 (2), IOAIN.2, IOAIN.3 (2), IOAIN.4 (2), IOAIN.5 (2), J1.1, J2.1, J3.1, J4.1, JP1.9, JP1.11, JP1.16, JP2.9, JP2.11, JP2.16

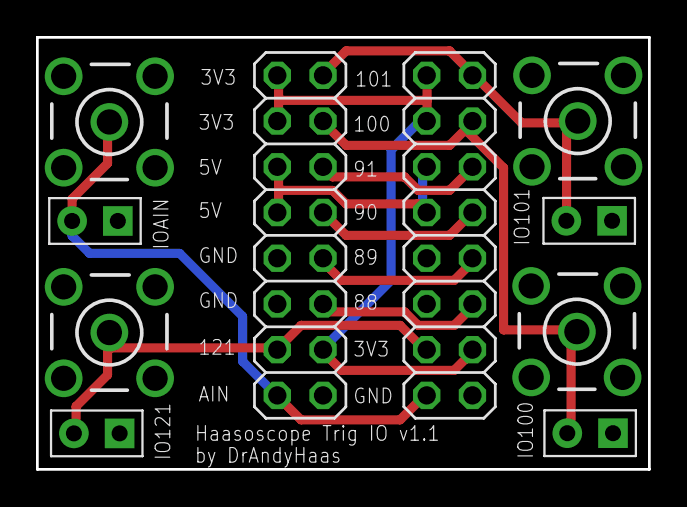
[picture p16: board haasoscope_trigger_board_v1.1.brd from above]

Board: 2 copper layers, 34.0 x 24.0 mm, 10 parts (0 on the bottom side), 11 nets.

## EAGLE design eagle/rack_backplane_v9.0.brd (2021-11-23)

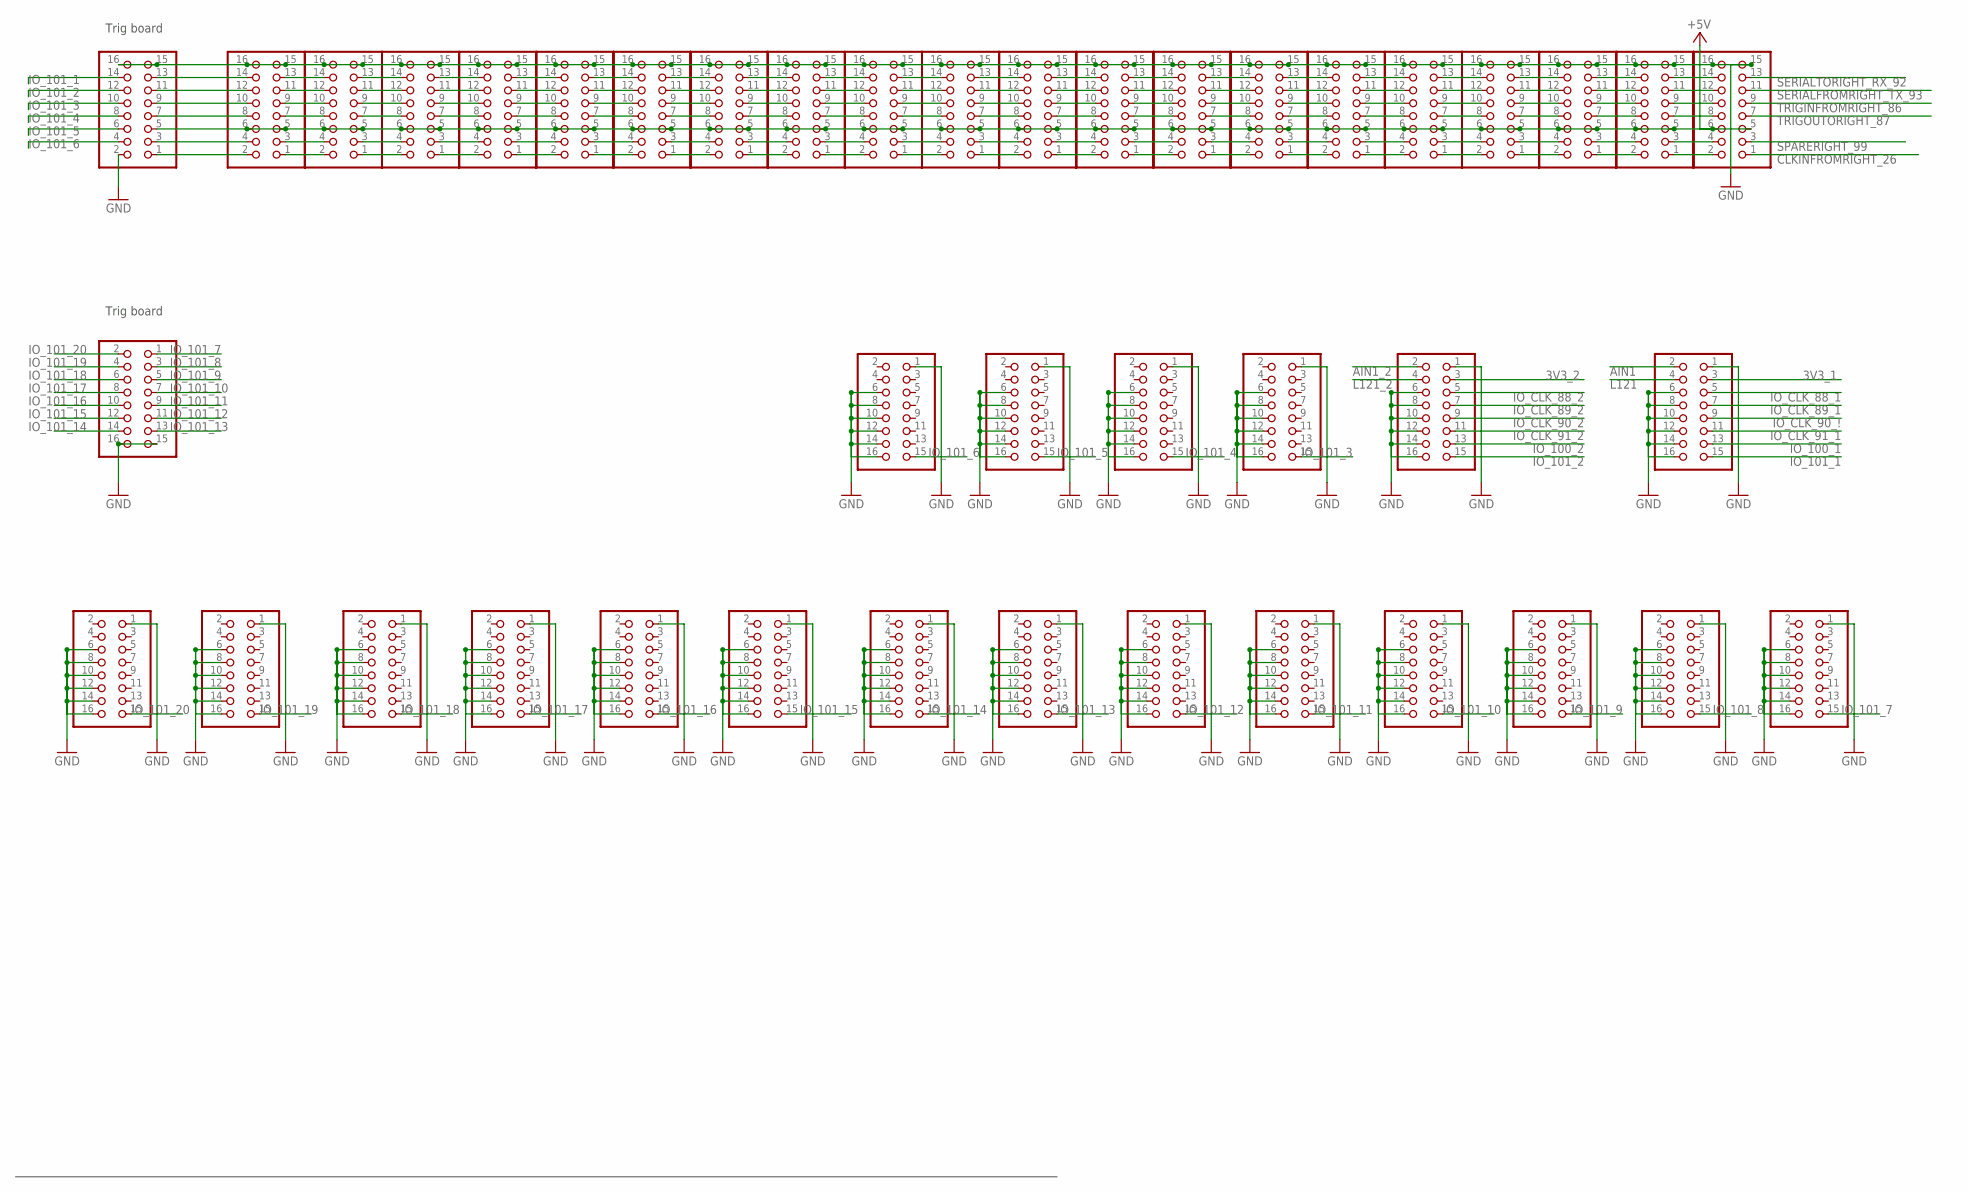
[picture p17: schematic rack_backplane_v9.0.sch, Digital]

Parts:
PIN_AIN_PWRGND1, PIN_AIN_PWRGND2, PIN_AIN_PWRGND3, PIN_AIN_PWRGND4, PIN_AIN_PWRGND5, PIN_AIN_PWRGND6, PIN_AIN_PWRGND7, PIN_AIN_PWRGND8, PIN_AIN_PWRGND9, PIN_AIN_PWRGND10, PIN_AIN_PWRGND11, PIN_AIN_PWRGND12, PIN_AIN_PWRGND13, PIN_AIN_PWRGND14, PIN_AIN_PWRGND15, PIN_AIN_PWRGND16, PIN_AIN_PWRGND17, PIN_AIN_PWRGND18, PIN_AIN_PWRGND19, PIN_AIN_PWRGND20, PIN_AIN_PWRGND21: 15-91-2160; 2X08; MPN 15-91-2160
PIN_ANALOG_1, PIN_ANALOG_2, PIN_ANALOG_3, PIN_ANALOG_4, PIN_ANALOG_5, PIN_ANALOG_6, PIN_ANALOG_7, PIN_ANALOG_8, PIN_ANALOG_9, PIN_ANALOG_10, PIN_ANALOG_11, PIN_ANALOG_12, PIN_ANALOG_13, PIN_ANALOG_14, PIN_ANALOG_15, PIN_ANALOG_16, PIN_ANALOG_17, PIN_ANALOG_18, PIN_ANALOG_19, PIN_ANALOG_20, PIN_ANALOG_21: 15-91-2160; 2X08; MPN 15-91-2160

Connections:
3V3_1: PIN_AIN_PWRGND1.3
3V3_2: PIN_AIN_PWRGND2.3
+5V: PIN_ANALOG_1.5, PIN_ANALOG_1.6, PIN_ANALOG_2.5, PIN_ANALOG_2.6, PIN_ANALOG_3.5, PIN_ANALOG_3.6, PIN_ANALOG_4.5, PIN_ANALOG_4.6, PIN_ANALOG_5.5, PIN_ANALOG_5.6, PIN_ANALOG_6.5, PIN_ANALOG_6.6, PIN_ANALOG_7.5, PIN_ANALOG_7.6, PIN_ANALOG_8.5, PIN_ANALOG_8.6, PIN_ANALOG_9.5, PIN_ANALOG_9.6, PIN_ANALOG_10.5, PIN_ANALOG_10.6, PIN_ANALOG_11.5, PIN_ANALOG_11.6, PIN_ANALOG_12.5, PIN_ANALOG_12.6, PIN_ANALOG_13.5, PIN_ANALOG_13.6, PIN_ANALOG_14.5, PIN_ANALOG_14.6, PIN_ANALOG_15.5, PIN_ANALOG_15.6, PIN_ANALOG_16.5, PIN_ANALOG_16.6, PIN_ANALOG_17.5, PIN_ANALOG_17.6, PIN_ANALOG_18.5, PIN_ANALOG_18.6, PIN_ANALOG_19.5, PIN_ANALOG_19.6, PIN_ANALOG_20.5, PIN_ANALOG_20.6, PIN_ANALOG_21.5
AIN1: PIN_AIN_PWRGND1.2
AIN1_2: PIN_AIN_PWRGND2.2
CLKINFROMRIGHT_26: PIN_ANALOG_1.1
GND: PIN_AIN_PWRGND1.1, PIN_AIN_PWRGND1.6, PIN_AIN_PWRGND1.8, PIN_AIN_PWRGND1.10, PIN_AIN_PWRGND1.12, PIN_AIN_PWRGND1.14, PIN_AIN_PWRGND1.16, PIN_AIN_PWRGND2.1, PIN_AIN_PWRGND2.6, PIN_AIN_PWRGND2.8, PIN_AIN_PWRGND2.10, PIN_AIN_PWRGND2.12, PIN_AIN_PWRGND2.14, PIN_AIN_PWRGND2.16, PIN_AIN_PWRGND3.1, PIN_AIN_PWRGND3.6, PIN_AIN_PWRGND3.8, PIN_AIN_PWRGND3.10, PIN_AIN_PWRGND3.12, PIN_AIN_PWRGND3.14, PIN_AIN_PWRGND3.16, PIN_AIN_PWRGND4.1, PIN_AIN_PWRGND4.6, PIN_AIN_PWRGND4.8, PIN_AIN_PWRGND4.10, PIN_AIN_PWRGND4.12, PIN_AIN_PWRGND4.14, PIN_AIN_PWRGND4.16, PIN_AIN_PWRGND5.1, PIN_AIN_PWRGND5.6, PIN_AIN_PWRGND5.8, PIN_AIN_PWRGND5.10, PIN_AIN_PWRGND5.12, PIN_AIN_PWRGND5.14, PIN_AIN_PWRGND5.16, PIN_AIN_PWRGND6.1, PIN_AIN_PWRGND6.6, PIN_AIN_PWRGND6.8, PIN_AIN_PWRGND6.10, PIN_AIN_PWRGND6.12, PIN_AIN_PWRGND6.14, PIN_AIN_PWRGND6.16, PIN_AIN_PWRGND7.1, PIN_AIN_PWRGND7.6, PIN_AIN_PWRGND7.8, PIN_AIN_PWRGND7.10, PIN_AIN_PWRGND7.12, PIN_AIN_PWRGND7.14, PIN_AIN_PWRGND7.16, PIN_AIN_PWRGND8.1, PIN_AIN_PWRGND8.6, PIN_AIN_PWRGND8.8, PIN_AIN_PWRGND8.10, PIN_AIN_PWRGND8.12, PIN_AIN_PWRGND8.14, PIN_AIN_PWRGND8.16, PIN_AIN_PWRGND9.1, PIN_AIN_PWRGND9.6, PIN_AIN_PWRGND9.8, PIN_AIN_PWRGND9.10, PIN_AIN_PWRGND9.12, PIN_AIN_PWRGND9.14, PIN_AIN_PWRGND9.16, PIN_AIN_PWRGND10.1, PIN_AIN_PWRGND10.6, PIN_AIN_PWRGND10.8, PIN_AIN_PWRGND10.10, PIN_AIN_PWRGND10.12, PIN_AIN_PWRGND10.14, PIN_AIN_PWRGND10.16, PIN_AIN_PWRGND11.1, PIN_AIN_PWRGND11.6, PIN_AIN_PWRGND11.8, PIN_AIN_PWRGND11.10, PIN_AIN_PWRGND11.12, PIN_AIN_PWRGND11.14, PIN_AIN_PWRGND11.16, PIN_AIN_PWRGND12.1, PIN_AIN_PWRGND12.6, PIN_AIN_PWRGND12.8, PIN_AIN_PWRGND12.10, PIN_AIN_PWRGND12.12, PIN_AIN_PWRGND12.14, PIN_AIN_PWRGND12.16, PIN_AIN_PWRGND13.1, PIN_AIN_PWRGND13.6, PIN_AIN_PWRGND13.8, PIN_AIN_PWRGND13.10, PIN_AIN_PWRGND13.12, PIN_AIN_PWRGND13.14, PIN_AIN_PWRGND13.16, PIN_AIN_PWRGND14.1, PIN_AIN_PWRGND14.6, PIN_AIN_PWRGND14.8, PIN_AIN_PWRGND14.10, PIN_AIN_PWRGND14.12, PIN_AIN_PWRGND14.14, PIN_AIN_PWRGND14.16, PIN_AIN_PWRGND15.1, PIN_AIN_PWRGND15.6, PIN_AIN_PWRGND15.8, PIN_AIN_PWRGND15.10, PIN_AIN_PWRGND15.12, PIN_AIN_PWRGND15.14, PIN_AIN_PWRGND15.16, PIN_AIN_PWRGND16.1, PIN_AIN_PWRGND16.6, PIN_AIN_PWRGND16.8, PIN_AIN_PWRGND16.10, PIN_AIN_PWRGND16.12, PIN_AIN_PWRGND16.14, PIN_AIN_PWRGND16.16, PIN_AIN_PWRGND17.1, PIN_AIN_PWRGND17.6, PIN_AIN_PWRGND17.8, PIN_AIN_PWRGND17.10, PIN_AIN_PWRGND17.12, PIN_AIN_PWRGND17.14, PIN_AIN_PWRGND17.16, PIN_AIN_PWRGND18.1, PIN_AIN_PWRGND18.6, PIN_AIN_PWRGND18.8, PIN_AIN_PWRGND18.10, PIN_AIN_PWRGND18.12, PIN_AIN_PWRGND18.14, PIN_AIN_PWRGND18.16, PIN_AIN_PWRGND19.1, PIN_AIN_PWRGND19.6, PIN_AIN_PWRGND19.8, PIN_AIN_PWRGND19.10, PIN_AIN_PWRGND19.12, PIN_AIN_PWRGND19.14, PIN_AIN_PWRGND19.16, PIN_AIN_PWRGND20.1, PIN_AIN_PWRGND20.6, PIN_AIN_PWRGND20.8, PIN_AIN_PWRGND20.10, PIN_AIN_PWRGND20.12, PIN_AIN_PWRGND20.14, PIN_AIN_PWRGND20.16, PIN_AIN_PWRGND21.15, PIN_AIN_PWRGND21.16, PIN_ANALOG_1.15, PIN_ANALOG_1.16, PIN_ANALOG_2.15, PIN_ANALOG_2.16, PIN_ANALOG_3.15, PIN_ANALOG_3.16, PIN_ANALOG_4.15, PIN_ANALOG_4.16, PIN_ANALOG_5.15, PIN_ANALOG_5.16, PIN_ANALOG_6.15, PIN_ANALOG_6.16, PIN_ANALOG_7.15, PIN_ANALOG_7.16, PIN_ANALOG_8.15, PIN_ANALOG_8.16, PIN_ANALOG_9.15, PIN_ANALOG_9.16, PIN_ANALOG_10.15, PIN_ANALOG_10.16, PIN_ANALOG_11.15, PIN_ANALOG_11.16, PIN_ANALOG_12.15, PIN_ANALOG_12.16, PIN_ANALOG_13.15, PIN_ANALOG_13.16, PIN_ANALOG_14.15, PIN_ANALOG_14.16, PIN_ANALOG_15.15, PIN_ANALOG_15.16, PIN_ANALOG_16.15, PIN_ANALOG_16.16, PIN_ANALOG_17.15, PIN_ANALOG_17.16, PIN_ANALOG_18.15, PIN_ANALOG_18.16, PIN_ANALOG_19.15, PIN_ANALOG_19.16, PIN_ANALOG_20.15, PIN_ANALOG_20.16, PIN_ANALOG_21.2, PIN_ANALOG_21.15, PIN_ANALOG_21.16
IO_100_1: PIN_AIN_PWRGND1.13
IO_100_2: PIN_AIN_PWRGND2.13
IO_101_1: PIN_AIN_PWRGND1.15, PIN_ANALOG_21.14
IO_101_2: PIN_AIN_PWRGND2.15, PIN_ANALOG_21.12
IO_101_3: PIN_AIN_PWRGND3.15, PIN_ANALOG_21.10
IO_101_4: PIN_AIN_PWRGND4.15, PIN_ANALOG_21.8
IO_101_5: PIN_AIN_PWRGND5.15, PIN_ANALOG_21.6
IO_101_6: PIN_AIN_PWRGND6.15, PIN_ANALOG_21.4
IO_101_7: PIN_AIN_PWRGND7.15, PIN_AIN_PWRGND21.1
IO_101_8: PIN_AIN_PWRGND8.15, PIN_AIN_PWRGND21.3
IO_101_9: PIN_AIN_PWRGND9.15, PIN_AIN_PWRGND21.5
IO_101_10: PIN_AIN_PWRGND10.15, PIN_AIN_PWRGND21.7
IO_101_11: PIN_AIN_PWRGND11.15, PIN_AIN_PWRGND21.9
IO_101_12: PIN_AIN_PWRGND12.15, PIN_AIN_PWRGND21.11
IO_101_13: PIN_AIN_PWRGND13.15, PIN_AIN_PWRGND21.13
IO_101_14: PIN_AIN_PWRGND14.15, PIN_AIN_PWRGND21.14
IO_101_15: PIN_AIN_PWRGND15.15, PIN_AIN_PWRGND21.12
IO_101_16: PIN_AIN_PWRGND16.15, PIN_AIN_PWRGND21.10
IO_101_17: PIN_AIN_PWRGND17.15, PIN_AIN_PWRGND21.8
IO_101_18: PIN_AIN_PWRGND18.15, PIN_AIN_PWRGND21.6
IO_101_19: PIN_AIN_PWRGND19.15, PIN_AIN_PWRGND21.4
IO_101_20: PIN_AIN_PWRGND20.15, PIN_AIN_PWRGND21.2
IO_CLK_88_1: PIN_AIN_PWRGND1.5
IO_CLK_88_2: PIN_AIN_PWRGND2.5
IO_CLK_89_1: PIN_AIN_PWRGND1.7
IO_CLK_89_2: PIN_AIN_PWRGND2.7
IO_CLK_90_2: PIN_AIN_PWRGND2.9
IO_CLK_90_!: PIN_AIN_PWRGND1.9
IO_CLK_91_1: PIN_AIN_PWRGND1.11
IO_CLK_91_2: PIN_AIN_PWRGND2.11
L121: PIN_AIN_PWRGND1.4
L121_2: PIN_AIN_PWRGND2.4
unnamed: PIN_ANALOG_1.14, PIN_ANALOG_2.13
unnamed: PIN_ANALOG_1.12, PIN_ANALOG_2.11
unnamed: PIN_ANALOG_1.10, PIN_ANALOG_2.9
unnamed: PIN_ANALOG_1.8, PIN_ANALOG_2.7
unnamed: PIN_ANALOG_1.4, PIN_ANALOG_2.3
unnamed: PIN_ANALOG_1.2, PIN_ANALOG_2.1
unnamed: PIN_ANALOG_2.2, PIN_ANALOG_3.1
unnamed: PIN_ANALOG_2.4, PIN_ANALOG_3.3
unnamed: PIN_ANALOG_2.8, PIN_ANALOG_3.7
unnamed: PIN_ANALOG_2.10, PIN_ANALOG_3.9
unnamed: PIN_ANALOG_2.12, PIN_ANALOG_3.11
unnamed: PIN_ANALOG_2.14, PIN_ANALOG_3.13
unnamed: PIN_ANALOG_3.2, PIN_ANALOG_4.1
unnamed: PIN_ANALOG_3.4, PIN_ANALOG_4.3
unnamed: PIN_ANALOG_3.8, PIN_ANALOG_4.7
unnamed: PIN_ANALOG_3.10, PIN_ANALOG_4.9
unnamed: PIN_ANALOG_3.12, PIN_ANALOG_4.11
unnamed: PIN_ANALOG_3.14, PIN_ANALOG_4.13
unnamed: PIN_ANALOG_4.2, PIN_ANALOG_5.1
unnamed: PIN_ANALOG_4.4, PIN_ANALOG_5.3
unnamed: PIN_ANALOG_4.8, PIN_ANALOG_5.7
unnamed: PIN_ANALOG_4.10, PIN_ANALOG_5.9
unnamed: PIN_ANALOG_4.12, PIN_ANALOG_5.11
unnamed: PIN_ANALOG_4.14, PIN_ANALOG_5.13
unnamed: PIN_ANALOG_5.2, PIN_ANALOG_6.1
unnamed: PIN_ANALOG_5.4, PIN_ANALOG_6.3
unnamed: PIN_ANALOG_5.8, PIN_ANALOG_6.7
unnamed: PIN_ANALOG_5.10, PIN_ANALOG_6.9
unnamed: PIN_ANALOG_5.12, PIN_ANALOG_6.11
unnamed: PIN_ANALOG_5.14, PIN_ANALOG_6.13
unnamed: PIN_ANALOG_6.2, PIN_ANALOG_7.1
unnamed: PIN_ANALOG_6.4, PIN_ANALOG_7.3
unnamed: PIN_ANALOG_6.8, PIN_ANALOG_7.7
unnamed: PIN_ANALOG_6.10, PIN_ANALOG_7.9
unnamed: PIN_ANALOG_6.12, PIN_ANALOG_7.11
unnamed: PIN_ANALOG_6.14, PIN_ANALOG_7.13
unnamed: PIN_ANALOG_7.2, PIN_ANALOG_8.1
unnamed: PIN_ANALOG_7.4, PIN_ANALOG_8.3
unnamed: PIN_ANALOG_7.8, PIN_ANALOG_8.7
unnamed: PIN_ANALOG_7.10, PIN_ANALOG_8.9
unnamed: PIN_ANALOG_7.12, PIN_ANALOG_8.11
unnamed: PIN_ANALOG_7.14, PIN_ANALOG_8.13
unnamed: PIN_ANALOG_8.2, PIN_ANALOG_9.1
unnamed: PIN_ANALOG_8.4, PIN_ANALOG_9.3
unnamed: PIN_ANALOG_8.8, PIN_ANALOG_9.7
unnamed: PIN_ANALOG_8.10, PIN_ANALOG_9.9
unnamed: PIN_ANALOG_8.12, PIN_ANALOG_9.11
unnamed: PIN_ANALOG_8.14, PIN_ANALOG_9.13
unnamed: PIN_ANALOG_9.2, PIN_ANALOG_10.1
unnamed: PIN_ANALOG_9.4, PIN_ANALOG_10.3
unnamed: PIN_ANALOG_9.8, PIN_ANALOG_10.7
unnamed: PIN_ANALOG_9.10, PIN_ANALOG_10.9
unnamed: PIN_ANALOG_9.12, PIN_ANALOG_10.11
unnamed: PIN_ANALOG_9.14, PIN_ANALOG_10.13
unnamed: PIN_ANALOG_10.2, PIN_ANALOG_11.1
unnamed: PIN_ANALOG_10.4, PIN_ANALOG_11.3
unnamed: PIN_ANALOG_10.8, PIN_ANALOG_11.7
unnamed: PIN_ANALOG_10.10, PIN_ANALOG_11.9
unnamed: PIN_ANALOG_10.12, PIN_ANALOG_11.11
unnamed: PIN_ANALOG_10.14, PIN_ANALOG_11.13
unnamed: PIN_ANALOG_11.2, PIN_ANALOG_12.1
unnamed: PIN_ANALOG_11.4, PIN_ANALOG_12.3
unnamed: PIN_ANALOG_11.8, PIN_ANALOG_12.7
unnamed: PIN_ANALOG_11.10, PIN_ANALOG_12.9
unnamed: PIN_ANALOG_11.12, PIN_ANALOG_12.11
unnamed: PIN_ANALOG_11.14, PIN_ANALOG_12.13
unnamed: PIN_ANALOG_12.2, PIN_ANALOG_13.1
unnamed: PIN_ANALOG_12.4, PIN_ANALOG_13.3
unnamed: PIN_ANALOG_12.8, PIN_ANALOG_13.7
unnamed: PIN_ANALOG_12.10, PIN_ANALOG_13.9
unnamed: PIN_ANALOG_12.12, PIN_ANALOG_13.11
unnamed: PIN_ANALOG_12.14, PIN_ANALOG_13.13
unnamed: PIN_ANALOG_13.2, PIN_ANALOG_14.1
unnamed: PIN_ANALOG_13.4, PIN_ANALOG_14.3
unnamed: PIN_ANALOG_13.8, PIN_ANALOG_14.7
unnamed: PIN_ANALOG_13.10, PIN_ANALOG_14.9
unnamed: PIN_ANALOG_13.12, PIN_ANALOG_14.11
unnamed: PIN_ANALOG_13.14, PIN_ANALOG_14.13
unnamed: PIN_ANALOG_14.2, PIN_ANALOG_15.1
unnamed: PIN_ANALOG_14.4, PIN_ANALOG_15.3
unnamed: PIN_ANALOG_14.8, PIN_ANALOG_15.7
unnamed: PIN_ANALOG_14.10, PIN_ANALOG_15.9
unnamed: PIN_ANALOG_14.12, PIN_ANALOG_15.11
unnamed: PIN_ANALOG_14.14, PIN_ANALOG_15.13
unnamed: PIN_ANALOG_15.2, PIN_ANALOG_16.1
unnamed: PIN_ANALOG_15.4, PIN_ANALOG_16.3
unnamed: PIN_ANALOG_15.8, PIN_ANALOG_16.7
unnamed: PIN_ANALOG_15.10, PIN_ANALOG_16.9
unnamed: PIN_ANALOG_15.12, PIN_ANALOG_16.11
unnamed: PIN_ANALOG_15.14, PIN_ANALOG_16.13
unnamed: PIN_ANALOG_16.2, PIN_ANALOG_17.1
unnamed: PIN_ANALOG_16.4, PIN_ANALOG_17.3
unnamed: PIN_ANALOG_16.8, PIN_ANALOG_17.7
unnamed: PIN_ANALOG_16.10, PIN_ANALOG_17.9
unnamed: PIN_ANALOG_16.12, PIN_ANALOG_17.11
unnamed: PIN_ANALOG_16.14, PIN_ANALOG_17.13
unnamed: PIN_ANALOG_17.2, PIN_ANALOG_18.1
unnamed: PIN_ANALOG_17.4, PIN_ANALOG_18.3
unnamed: PIN_ANALOG_17.8, PIN_ANALOG_18.7
unnamed: PIN_ANALOG_17.10, PIN_ANALOG_18.9
unnamed: PIN_ANALOG_17.12, PIN_ANALOG_18.11
unnamed: PIN_ANALOG_17.14, PIN_ANALOG_18.13
unnamed: PIN_ANALOG_18.2, PIN_ANALOG_19.1
unnamed: PIN_ANALOG_18.4, PIN_ANALOG_19.3
unnamed: PIN_ANALOG_18.8, PIN_ANALOG_19.7
unnamed: PIN_ANALOG_18.10, PIN_ANALOG_19.9
unnamed: PIN_ANALOG_18.12, PIN_ANALOG_19.11
unnamed: PIN_ANALOG_18.14, PIN_ANALOG_19.13
unnamed: PIN_ANALOG_19.2, PIN_ANALOG_20.1
unnamed: PIN_ANALOG_19.4, PIN_ANALOG_20.3
unnamed: PIN_ANALOG_19.8, PIN_ANALOG_20.7
unnamed: PIN_ANALOG_19.10, PIN_ANALOG_20.9
unnamed: PIN_ANALOG_19.12, PIN_ANALOG_20.11
unnamed: PIN_ANALOG_19.14, PIN_ANALOG_20.13
unnamed: PIN_ANALOG_20.2, PIN_ANALOG_21.1
unnamed: PIN_ANALOG_20.4, PIN_ANALOG_21.3
unnamed: PIN_ANALOG_20.8, PIN_ANALOG_21.7
unnamed: PIN_ANALOG_20.10, PIN_ANALOG_21.9
unnamed: PIN_ANALOG_20.12, PIN_ANALOG_21.11
unnamed: PIN_ANALOG_20.14, PIN_ANALOG_21.13
SERIALFROMRIGHT_TX_93: PIN_ANALOG_1.11
SERIALTORIGHT_RX_92: PIN_ANALOG_1.13
SPARERIGHT_99: PIN_ANALOG_1.3
TRIGINFROMRIGHT_86: PIN_ANALOG_1.9
TRIGOUTORIGHT_87: PIN_ANALOG_1.7

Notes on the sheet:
Trig board

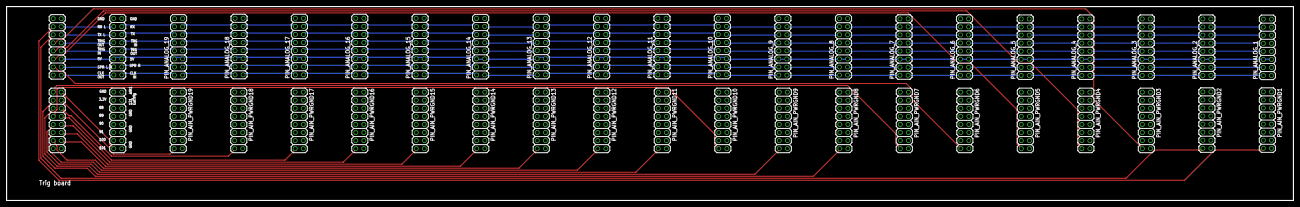
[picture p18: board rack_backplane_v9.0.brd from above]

Board: 4 copper layers, 405.1 x 61.0 mm, 43 parts (1 on the bottom side), 142 nets.

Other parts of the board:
GOLD_ORB_SM1: OSHWLOGOLOGO8MM; OSHW_8MM

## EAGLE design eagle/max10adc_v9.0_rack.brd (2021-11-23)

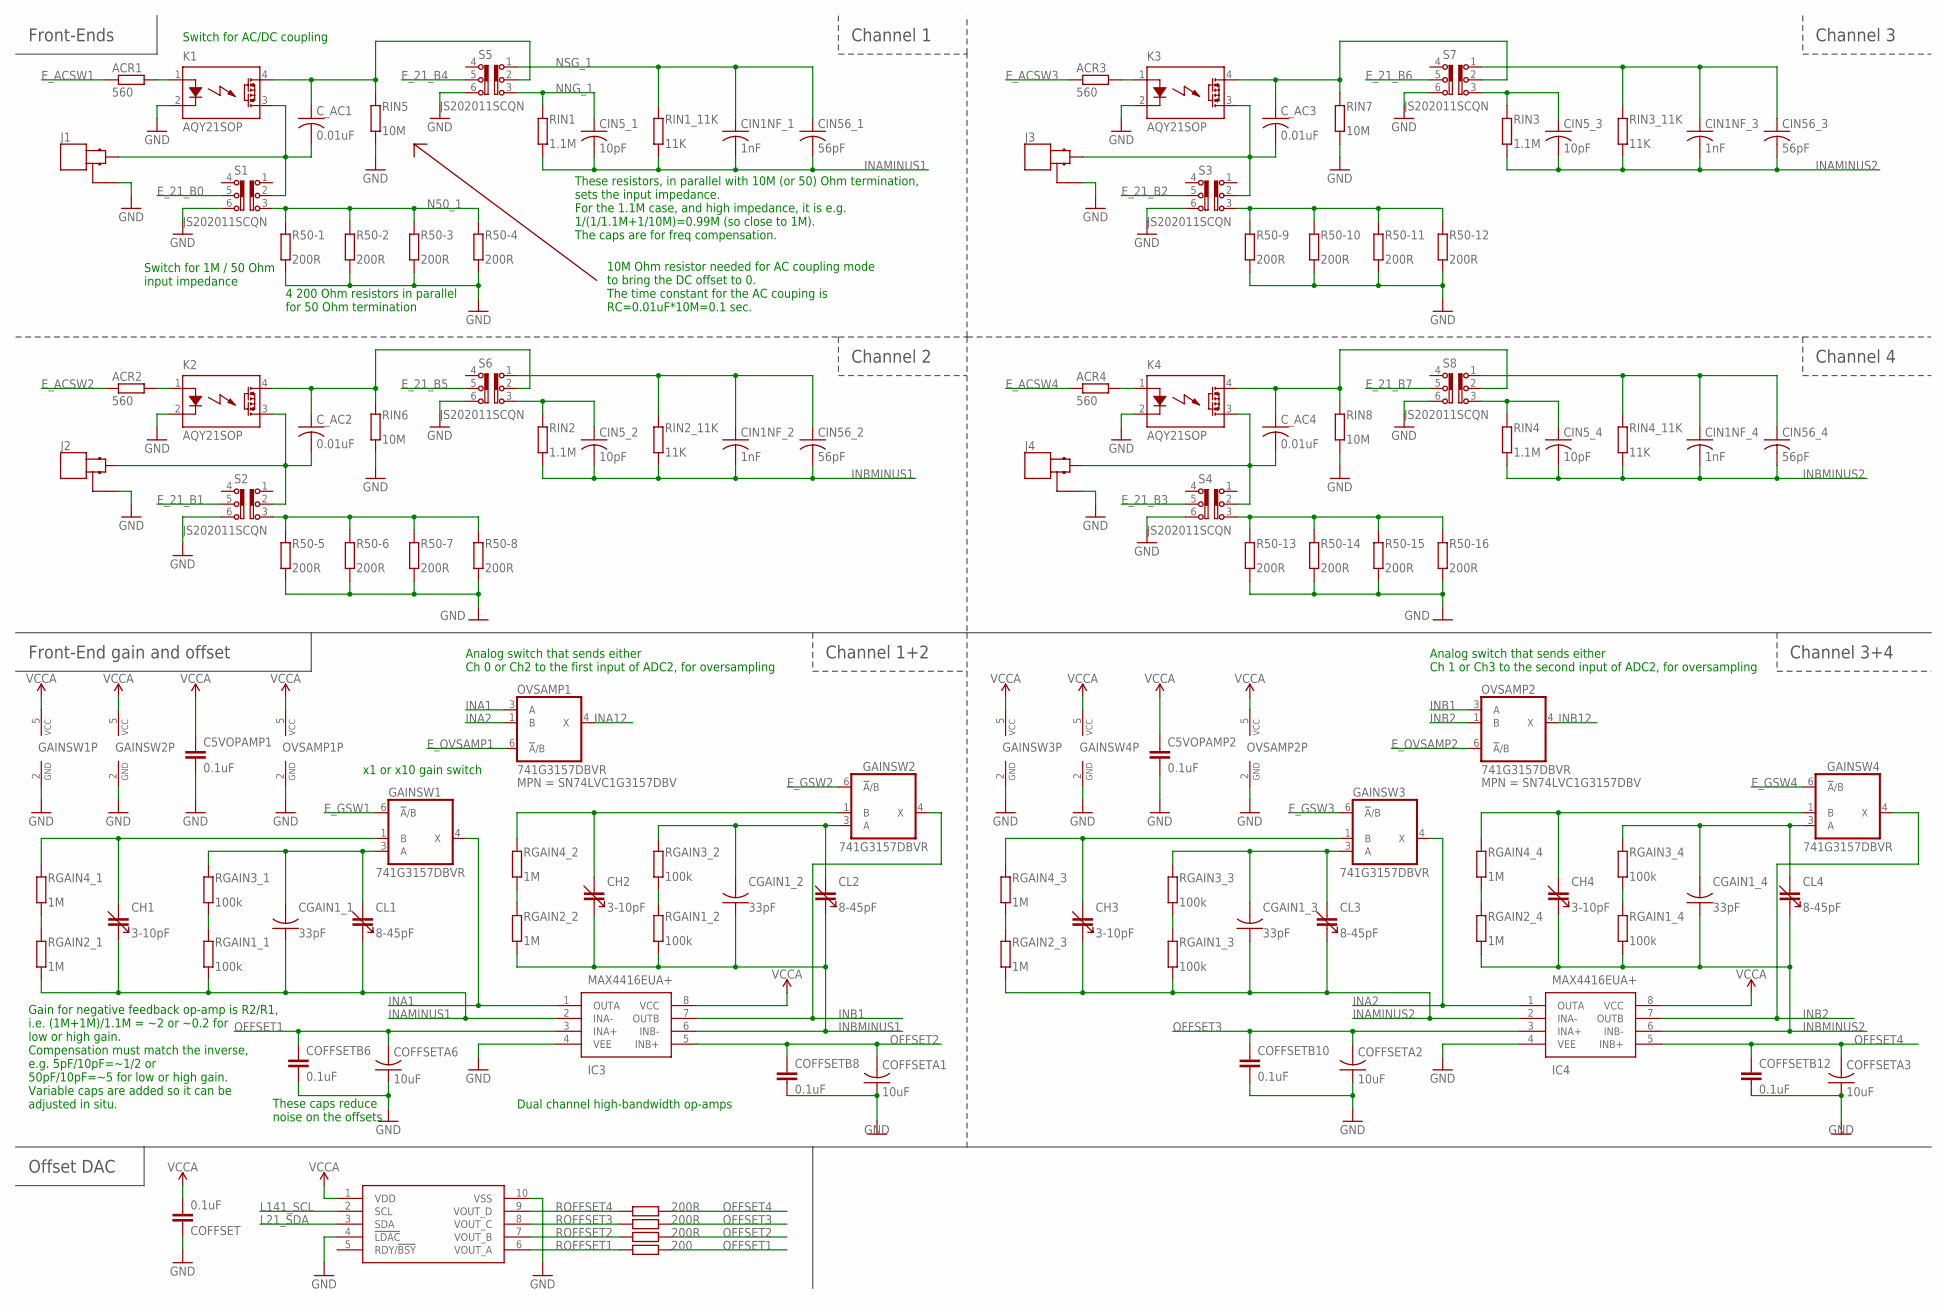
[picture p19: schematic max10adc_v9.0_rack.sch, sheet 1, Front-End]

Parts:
ACR1, ACR2, ACR3, ACR4: 560; R0805; MPN MF-RES-0805-560
C5VOPAMP1, C5VOPAMP2: 0.1uF; C0805K; MPN MF-CAP-0805-0.1uF
CGAIN1_1, CGAIN1_2, CGAIN1_3, CGAIN1_4: 33pF; C0603; MPN 06033A330JAT2A
CH1, CH2, CH3, CH4: 3-10pF; CTZ3; MPN TZY2Z100AC01
CIN1NF_1, CIN1NF_2, CIN1NF_3, CIN1NF_4: 1nF; C0603; MPN 06035A102JAT2A
CIN5_1, CIN5_2, CIN5_3, CIN5_4: 10pF; C0603; MPN MF-CAP-0603-10pF
CIN56_1, CIN56_2, CIN56_3, CIN56_4: 56pF; C0603; MPN 06035A560FAT2A
CL1, CL2, CL3, CL4: 8-45pF; CTZ3; MPN TZY2K450AC01
COFFSET: 0.1uF; C0805K; MPN MF-CAP-0805-0.1uF
COFFSETA1, COFFSETA2, COFFSETA3, COFFSETA6: 10uF; C1206; MPN MF-CAP-1206-10uF
COFFSETB6, COFFSETB8, COFFSETB10, COFFSETB12: 0.1uF; C0805K; MPN MF-CAP-0805-0.1uF
C_AC1, C_AC2, C_AC3, C_AC4: 0.01uF; C0603
DAC1: MCP4728; MSOP10
GAINSW1, GAINSW2, GAINSW3, GAINSW4: 741G3157DBVR; DBV_R-PDSO-G6; MPN SN74LVC1G3157DBV
IC3, IC4: MAX4416EUA+; SOP65P490X110-8N
J1, J2, J3, J4: MOLEX_BNC_73100-0105; MOLEX-BNC-73100-0105; MPN 73100-0105
K1, K2, K3, K4: AQY21SOP; SOP04; MPN AQY210S
OVSAMP1, OVSAMP2: 741G3157DBVR; DBV_R-PDSO-G6; MPN SN74LVC1G3157DBV
R50-1, R50-2, R50-3, R50-4, R50-5, R50-6, R50-7, R50-8, R50-9, R50-10, R50-11, R50-12, R50-13, R50-14, R50-15, R50-16: 200R; R0805
RGAIN1_1, RGAIN1_2, RGAIN1_3, RGAIN1_4, RGAIN3_1, RGAIN3_2, RGAIN3_3, RGAIN3_4: 100k; R0805; MPN MF-RES-0805-100k
RGAIN2_1, RGAIN2_2, RGAIN2_3, RGAIN2_4, RGAIN4_1, RGAIN4_2, RGAIN4_3, RGAIN4_4: 1M; R0805; MPN MF-RES-0805-1M
RIN1, RIN2, RIN3, RIN4: 1.1M; R0805; MPN CRCW08051M10FKEA
RIN1_11K, RIN2_11K, RIN3_11K, RIN4_11K: 11K; R0805; MPN CRCW080511K0FKEA
RIN5, RIN6, RIN7, RIN8: 10M; R0805; MPN CRCW080510M0FKEB
ROFFSET1: 200; R0805
ROFFSET2, ROFFSET3, ROFFSET4: 200R; R0805
S1, S2, S3, S4, S5, S6, S7, S8: JS202011SCQN

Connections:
CGAIN1: CGAIN1_1.2, CL1.- (4), GAINSW1.3 (A), RGAIN3_1.1
CGAIN2: CH1.- (4), GAINSW1.1 (B), RGAIN4_1.1
CGAIN3: CGAIN1_2.2, CL2.- (4), GAINSW2.3 (A), RGAIN3_2.1
CGAIN4: CH2.- (4), GAINSW2.1 (B), RGAIN4_2.1
CGAIN5: CGAIN1_3.2, CL3.- (4), GAINSW3.3 (A), RGAIN3_3.1
CGAIN6: CH3.- (4), GAINSW3.1 (B), RGAIN4_3.1
CGAIN7: CGAIN1_4.2, CL4.- (4), GAINSW4.3 (A), RGAIN3_4.1
CGAIN8: CH4.- (4), GAINSW4.1 (B), RGAIN4_4.1
E_21_B0: S1.5; also elsewhere on the board
E_21_B1: S2.5; also elsewhere on the board
E_21_B2: S3.5; also elsewhere on the board
E_21_B3: S4.5; also elsewhere on the board
E_21_B4: S5.5; also elsewhere on the board
E_21_B5: S6.5; also elsewhere on the board
E_21_B6: S7.5; also elsewhere on the board
E_21_B7: S8.5; also elsewhere on the board
E_ACSW1: ACR1.1; also elsewhere on the board
E_ACSW2: ACR2.1; also elsewhere on the board
E_ACSW3: ACR3.1; also elsewhere on the board
E_ACSW4: ACR4.1; also elsewhere on the board
E_GSW1: GAINSW1.6 (!A!/B); also elsewhere on the board
E_GSW2: GAINSW2.6 (!A!/B); also elsewhere on the board
E_GSW3: GAINSW3.6 (!A!/B); also elsewhere on the board
E_GSW4: GAINSW4.6 (!A!/B); also elsewhere on the board
E_OVSAMP1: OVSAMP1.6 (!A!/B); also elsewhere on the board
E_OVSAMP2: OVSAMP2.6 (!A!/B); also elsewhere on the board
GND: C5VOPAMP1.2, C5VOPAMP2.2, COFFSET.1, COFFSETA1.1, COFFSETA2.1, COFFSETA3.1, COFFSETA6.1, COFFSETB6.1, COFFSETB8.1, COFFSETB10.1, COFFSETB12.1, DAC1.4 (!LDAC), DAC1.10 (VSS), GAINSW1.2 (GND), GAINSW2.2 (GND), GAINSW3.2 (GND), GAINSW4.2 (GND), IC3.4 (VEE), IC4.4 (VEE), J1.GND1 (GND), J1.GND2 (GND), J2.GND1 (GND), J2.GND2 (GND), J3.GND1 (GND), J3.GND2 (GND), J4.GND1 (GND), J4.GND2 (GND), K1.2 (K), K2.2 (K), K3.2 (K), K4.2 (K), OVSAMP1.2 (GND), OVSAMP2.2 (GND), R50-1.2, R50-2.2, R50-3.2, R50-4.2, R50-5.2, R50-6.2, R50-7.2, R50-8.2, R50-9.2, R50-10.2, R50-11.2, R50-12.2, R50-13.2, R50-14.2, R50-15.2, R50-16.2, RIN5.2, RIN6.2, RIN7.2, RIN8.2, S1.6, S2.6, S3.6, S4.6, S5.6, S6.6, S7.6, S8.6; also elsewhere on the board
INA1: GAINSW1.4 (X), IC3.1 (OUTA), OVSAMP1.3 (A); also elsewhere on the board
INA2: GAINSW3.4 (X), IC4.1 (OUTA), OVSAMP1.1 (B)
INA12: OVSAMP1.4 (X); also elsewhere on the board
INAMINUS1: CGAIN1_1.1, CH1.+ (3), CIN1NF_1.2, CIN5_1.2, CIN56_1.2, CL1.+ (3), IC3.2 (INA-), RGAIN1_1.2, RGAIN2_1.2, RIN1.2, RIN1_11K.2
INAMINUS2: CGAIN1_3.1, CH3.+ (3), CIN1NF_3.2, CIN5_3.2, CIN56_3.2, CL3.+ (3), IC4.2 (INA-), RGAIN1_3.2, RGAIN2_3.2, RIN3.2, RIN3_11K.2
INB1: GAINSW2.4 (X), IC3.7 (OUTB), OVSAMP2.3 (A); also elsewhere on the board
INB2: GAINSW4.4 (X), IC4.7 (OUTB), OVSAMP2.1 (B)
INB12: OVSAMP2.4 (X); also elsewhere on the board
INBMINUS1: CGAIN1_2.1, CH2.+ (3), CIN1NF_2.2, CIN5_2.2, CIN56_2.2, CL2.+ (3), IC3.6 (INB-), RGAIN1_2.2, RGAIN2_2.2, RIN2.2, RIN2_11K.2
INBMINUS2: CGAIN1_4.1, CH4.+ (3), CIN1NF_4.2, CIN5_4.2, CIN56_4.2, CL4.+ (3), IC4.6 (INB-), RGAIN1_4.2, RGAIN2_4.2, RIN4.2, RIN4_11K.2
INJ1: C_AC1.2, J1.SIGNAL, K1.3 (DS2), S1.2
INJ2: C_AC2.2, J2.SIGNAL, K2.3 (DS2), S2.2
INJ3: C_AC3.2, J3.SIGNAL, K3.3 (DS2), S3.2
INJ4: C_AC4.2, J4.SIGNAL, K4.3 (DS2), S4.2
L21_SDA: DAC1.3 (SDA); also elsewhere on the board
L141_SCL: DAC1.2 (SCL); also elsewhere on the board
N50_1: R50-1.1, R50-2.1, R50-3.1, R50-4.1, S1.3
unnamed: RGAIN1_1.1, RGAIN3_1.2
unnamed: RGAIN2_1.1, RGAIN4_1.2
unnamed: RGAIN1_2.1, RGAIN3_2.2
unnamed: RGAIN2_2.1, RGAIN4_2.2
unnamed: RGAIN1_3.1, RGAIN3_3.2
unnamed: RGAIN2_3.1, RGAIN4_3.2
unnamed: RGAIN1_4.1, RGAIN3_4.2
unnamed: RGAIN2_4.1, RGAIN4_4.2
unnamed: C_AC1.1, K1.4 (DS1), RIN5.1, S5.2
unnamed: ACR1.2, K1.1 (A)
unnamed: C_AC2.1, K2.4 (DS1), RIN6.1, S6.2
unnamed: CIN1NF_2.1, CIN56_2.1, RIN2_11K.1, S6.1
unnamed: ACR2.2, K2.1 (A)
unnamed: CIN5_2.1, RIN2.1, S6.3
unnamed: R50-5.1, R50-6.1, R50-7.1, R50-8.1, S2.3
unnamed: R50-9.1, R50-10.1, R50-11.1, R50-12.1, S3.3
unnamed: R50-13.1, R50-14.1, R50-15.1, R50-16.1, S4.3
unnamed: ACR3.2, K3.1 (A)
unnamed: ACR4.2, K4.1 (A)
unnamed: C_AC3.1, K3.4 (DS1), RIN7.1, S7.2
unnamed: CIN1NF_3.1, CIN56_3.1, RIN3_11K.1, S7.1
unnamed: DAC1.6 (VOUT_A), ROFFSET1.2
unnamed: DAC1.7 (VOUT_B), ROFFSET2.2
unnamed: DAC1.8 (VOUT_C), ROFFSET3.2
unnamed: DAC1.9 (VOUT_D), ROFFSET4.2
unnamed: C_AC4.1, K4.4 (DS1), RIN8.1, S8.2
unnamed: CIN5_3.1, RIN3.1, S7.3
unnamed: CIN1NF_4.1, CIN56_4.1, RIN4_11K.1, S8.1
unnamed: CIN5_4.1, RIN4.1, S8.3
NNG_1: CIN5_1.1, RIN1.1, S5.3
NSG_1: CIN1NF_1.1, CIN56_1.1, RIN1_11K.1, S5.1
OFFSET1: COFFSETA6.2, COFFSETB6.2, IC3.3 (INA+), ROFFSET1.1
OFFSET2: COFFSETA1.2, COFFSETB8.2, IC3.5 (INB+), ROFFSET2.1
OFFSET3: COFFSETA2.2, COFFSETB10.2, IC4.3 (INA+), ROFFSET3.1
OFFSET4: COFFSETA3.2, COFFSETB12.2, IC4.5 (INB+), ROFFSET4.1
VCCA: C5VOPAMP1.1, C5VOPAMP2.1, COFFSET.2, DAC1.1 (VDD), GAINSW1.5 (VCC), GAINSW2.5 (VCC), GAINSW3.5 (VCC), GAINSW4.5 (VCC), IC3.8 (VCC), IC4.8 (VCC), OVSAMP1.5 (VCC), OVSAMP2.5 (VCC); also elsewhere on the board

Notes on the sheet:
Front-Ends
Channel 3
Channel 1
Channel 2
Channel 4
Front-End gain and offset
Channel 1+2
Channel 3+4
Offset DAC
4 200 Ohm resistors in parallel for 50 Ohm termination
10M Ohm resistor needed for AC coupling mode to bring the DC offset to 0. The time constant for the AC couping is RC=0.01uF*10M=0.1 sec.
These resistors, in parallel with 10M (or 50) Ohm termination, sets the input impedance. For the 1.1M case, and high impedance, it is e.g. 1/(1/1.1M+1/10M)=0.99M (so close to 1M). The caps are for freq compensation.
Switch for AC/DC coupling
Switch for 1M / 50 Ohm input impedance
Analog switch that sends either Ch 0 or Ch2 to the first input of ADC2, for oversampling
Analog switch that sends either Ch 1 or Ch3 to the second input of ADC2, for oversampling
Dual channel high-bandwidth op-amps
x1 or x10 gain switch
These caps reduce noise on the offsets
Gain for negative feedback op-amp is R2/R1, i.e. (1M+1M)/1.1M = ~2 or ~0.2 for low or high gain. Compensation must match the inverse, e.g. 5pF/10pF=~1/2 or 50pF/10pF=~5 for low or high gain. Variable caps are added so it can be adjusted in situ.

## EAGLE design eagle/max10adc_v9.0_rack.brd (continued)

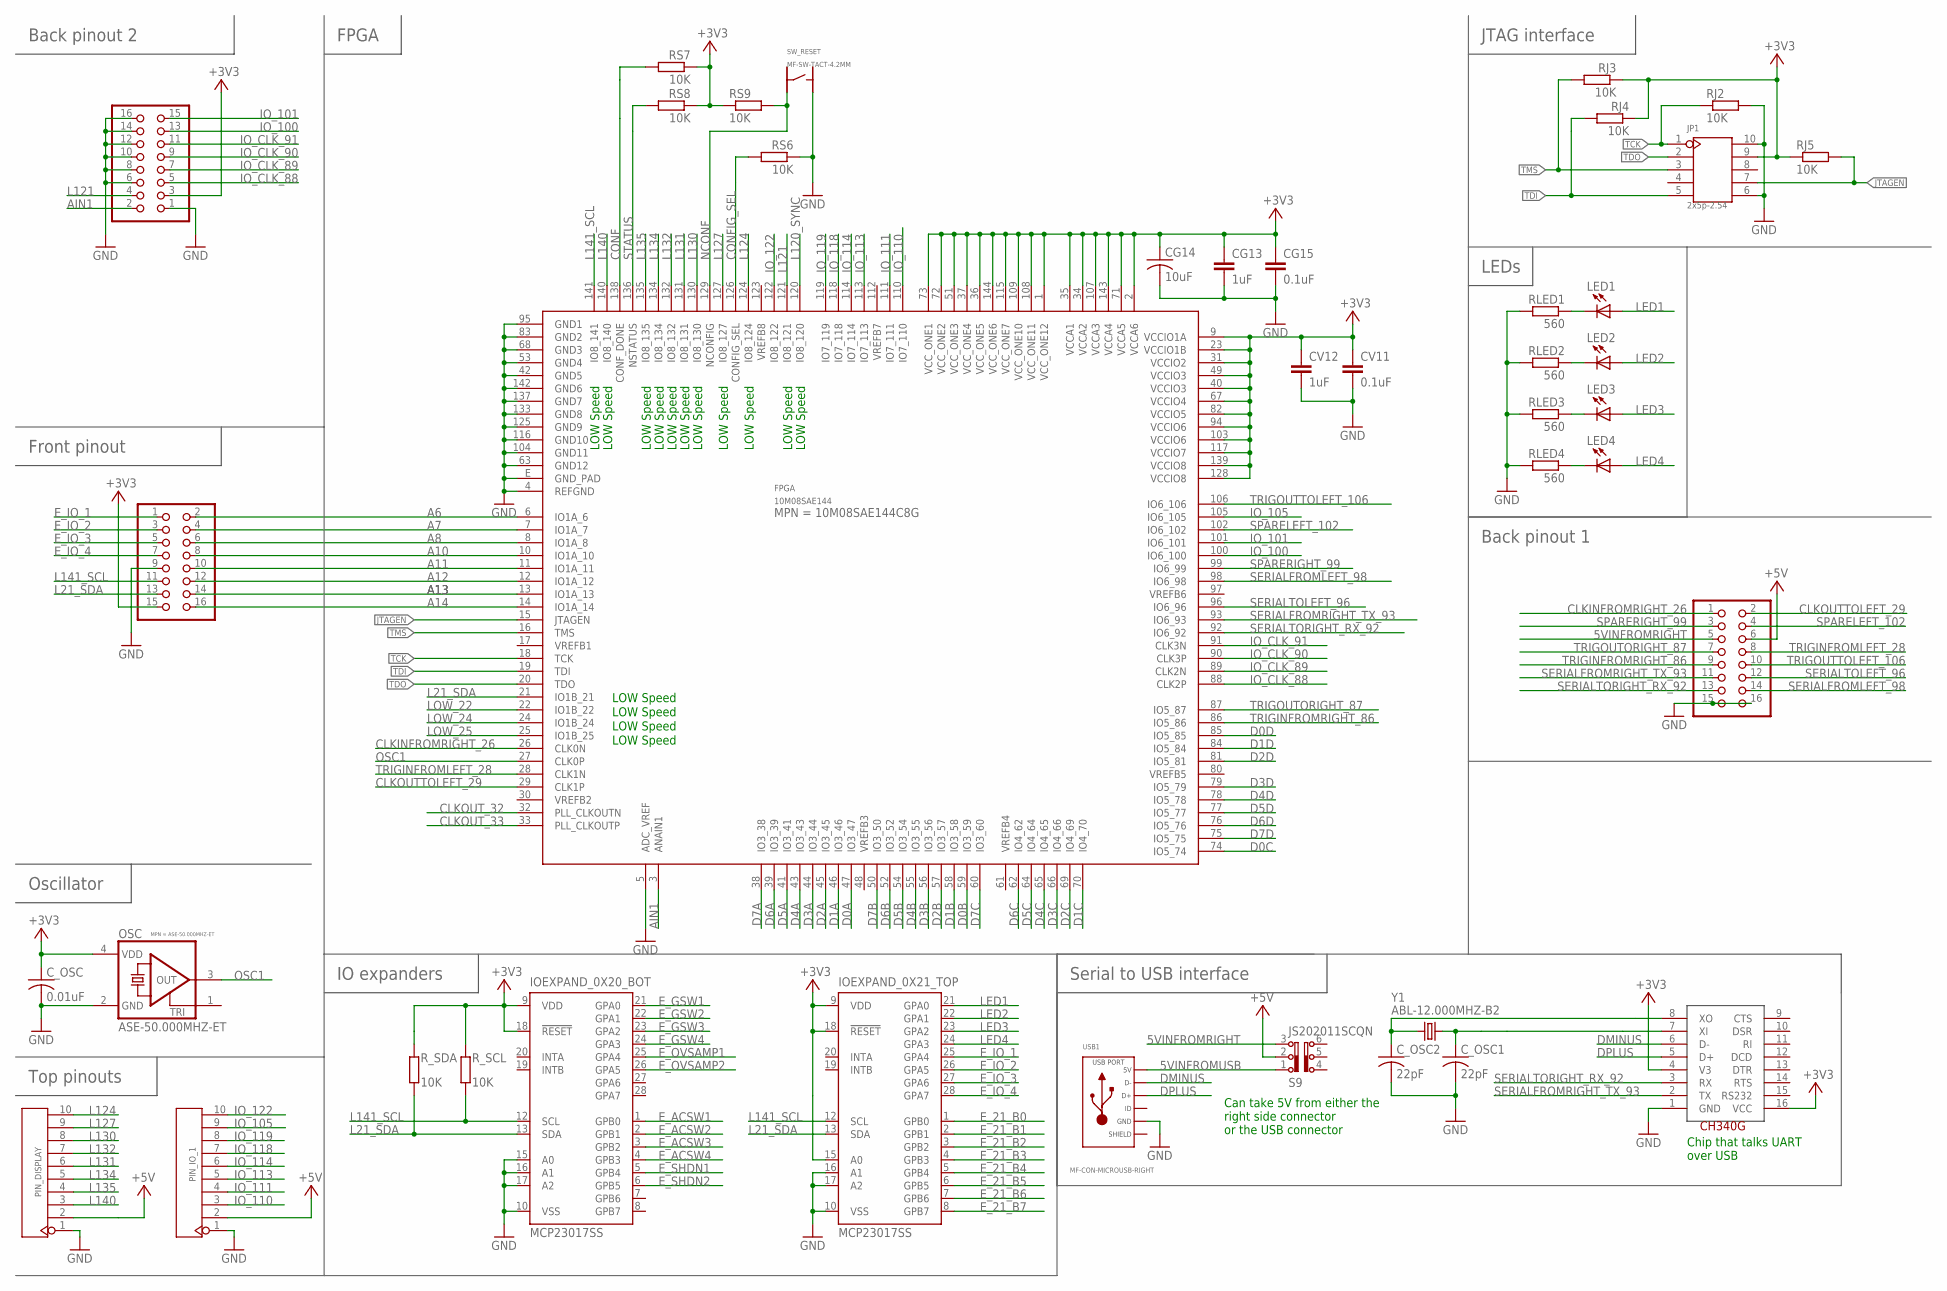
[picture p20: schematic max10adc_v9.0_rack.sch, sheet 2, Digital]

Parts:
CG13: 1uF; C0805K; MPN MF-CAP-0805-1uF
CG14: 10uF; C1206; MPN MF-CAP-1206-10uF
CG15: 0.1uF; C0805K; MPN MF-CAP-0805-0.1uF
CV11: 0.1uF; C0805K; MPN MF-CAP-0805-0.1uF
CV12: 1uF; C0805K; MPN MF-CAP-0805-1uF
C_OSC: 0.01uF; C0603
C_OSC1, C_OSC2: 22pF; C0603
FPGA: 10M08SAE144; EQFP144; MPN 10M08SAE144C8G
IOEXPAND_0X20_BOT, IOEXPAND_0X21_TOP: MCP23017SS; SSOP28
JP1: 2x5p-2.54; H2X5-2.54
LED1, LED2, LED3, LED4: MF-LED-0805-RED; SML0805; MPN MF-LED-0805-RED
OSC: ASE-50.000MHZ-ET; ASE; MPN ASE-50.000MHZ-ET
PIN_AIN_IO2_PWRGND: 15-91-2160; 2X08/90; MPN 15-91-2160
PIN_ANALOG_IOEXP, PIN_ANALOG_IOEXP1: 15-91-2160; 2X08/90; MPN 15-91-2160
PIN_DISPLAY: YELLOW-10P-2.54; H10-2.54
PIN_IO_1: YELLOW-10P-2.54; H10-2.54
RJ2, RJ3, RJ4, RJ5: 10K; R0805; MPN MF-RES-0805-10K
RLED1, RLED2, RLED3, RLED4: 560; R0805; MPN MF-RES-0805-560
RS6, RS7, RS8, RS9: 10K; R0805; MPN MF-RES-0805-10K
R_SCL: 10K; R0805; MPN MF-RES-0805-10K
R_SDA: 10K; R0805; MPN MF-RES-0805-10K
S9: JS202011SCQN
SW_RESET: MF-SW-TACT-4.2MM; TACT4.2MM
U340G: CH340G; SOIC16
USB1: MF-CON-MICROUSB-RIGHT; 10118193-0001LF
Y1: ABL-12.000MHZ-B2; HC49US

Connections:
5VINFROMRIGHT: PIN_ANALOG_IOEXP1.5, S9.3
5VINFROMUSB: S9.1, USB1.1 (5V)
+3V3: CG13.1, CG14.1, CG15.1, CV11.1, CV12.1, C_OSC.1, FPGA.1 (VCC_ONE12), FPGA.2 (VCCA6), FPGA.9 (VCCIO1A), FPGA.23 (VCCIO1B), FPGA.31 (VCCIO2), FPGA.34 (VCCA2), FPGA.35 (VCCA1), FPGA.36 (VCC_ONE5), FPGA.37 (VCC_ONE4), FPGA.40 (VCCIO3), FPGA.49 (VCCIO3), FPGA.51 (VCC_ONE3), FPGA.67 (VCCIO4), FPGA.71 (VCCA5), FPGA.72 (VCC_ONE2), FPGA.73 (VCC_ONE1), FPGA.82 (VCCIO5), FPGA.94 (VCCIO6), FPGA.103 (VCCIO6), FPGA.107 (VCCA3), FPGA.108 (VCC_ONE11), FPGA.109 (VCC_ONE10), FPGA.115 (VCC_ONE7), FPGA.117 (VCCIO7), FPGA.128 (VCCIO8), FPGA.139 (VCCIO8), FPGA.143 (VCCA4), FPGA.144 (VCC_ONE6), IOEXPAND_0X20_BOT.9 (VDD), IOEXPAND_0X20_BOT.18 (!RESET), IOEXPAND_0X21_TOP.9 (VDD), IOEXPAND_0X21_TOP.15 (A0), IOEXPAND_0X21_TOP.18 (!RESET), JP1.9, OSC.4 (VDD), PIN_AIN_IO2_PWRGND.3, PIN_ANALOG_IOEXP.15, RJ3.1, RJ4.1, RJ5.1, RS7.1, RS8.1, RS9.1, R_SCL.2, R_SDA.2, U340G.4 (V3), U340G.16 (VCC); also elsewhere on the board
+5V: PIN_ANALOG_IOEXP1.6, PIN_DISPLAY.2, PIN_IO_1.2, S9.2; also elsewhere on the board
A6: FPGA.6 (IO1A_6), PIN_ANALOG_IOEXP.2
A7: FPGA.7 (IO1A_7), PIN_ANALOG_IOEXP.4
A8: FPGA.8 (IO1A_8), PIN_ANALOG_IOEXP.6
A10: FPGA.10 (IO1A_10), PIN_ANALOG_IOEXP.8
A11: FPGA.11 (IO1A_11), PIN_ANALOG_IOEXP.10
A12: FPGA.12 (IO1A_12), PIN_ANALOG_IOEXP.12
A13: FPGA.13 (IO1A_13), PIN_ANALOG_IOEXP.14
A14: FPGA.14 (IO1A_14), PIN_ANALOG_IOEXP.16
AIN1: FPGA.3 (ANAIN1), PIN_AIN_IO2_PWRGND.2
CLKINFROMRIGHT_26: FPGA.26 (CLK0N), PIN_ANALOG_IOEXP1.1
CLKOUTTOLEFT_29: FPGA.29 (CLK1P), PIN_ANALOG_IOEXP1.2
CLKOUT_32: FPGA.32 (PLL_CLKOUTN); also elsewhere on the board
CLKOUT_33: FPGA.33 (PLL_CLKOUTP); also elsewhere on the board
CONF: FPGA.138 (CONF_DONE), RS7.2
CONFIG_SEL: FPGA.126 (CONFIG_SEL), RS6.2
D0A: FPGA.47 (IO3_47); also elsewhere on the board
D0B: FPGA.59 (IO3_59); also elsewhere on the board
D0C: FPGA.74 (IO5_74); also elsewhere on the board
D0D: FPGA.85 (IO5_85); also elsewhere on the board
D1A: FPGA.46 (IO3_46); also elsewhere on the board
D1B: FPGA.58 (IO3_58); also elsewhere on the board
D1C: FPGA.70 (IO4_70); also elsewhere on the board
D1D: FPGA.84 (IO5_84); also elsewhere on the board
D2A: FPGA.45 (IO3_45); also elsewhere on the board
D2B: FPGA.57 (IO3_57); also elsewhere on the board
D2C: FPGA.69 (IO4_69); also elsewhere on the board
D2D: FPGA.81 (IO5_81); also elsewhere on the board
D3A: FPGA.44 (IO3_44); also elsewhere on the board
D3B: FPGA.56 (IO3_56); also elsewhere on the board
D3C: FPGA.66 (IO4_66); also elsewhere on the board
D3D: FPGA.79 (IO5_79); also elsewhere on the board
D4A: FPGA.43 (IO3_43); also elsewhere on the board
D4B: FPGA.55 (IO3_55); also elsewhere on the board
D4C: FPGA.65 (IO4_65); also elsewhere on the board
D4D: FPGA.78 (IO5_78); also elsewhere on the board
D5A: FPGA.41 (IO3_41); also elsewhere on the board
D5B: FPGA.54 (IO3_54); also elsewhere on the board
D5C: FPGA.64 (IO4_64); also elsewhere on the board
D5D: FPGA.77 (IO5_77); also elsewhere on the board
D6A: FPGA.39 (IO3_39); also elsewhere on the board
D6B: FPGA.52 (IO3_52); also elsewhere on the board
D6C: FPGA.62 (IO4_62); also elsewhere on the board
D6D: FPGA.76 (IO5_76); also elsewhere on the board
D7A: FPGA.38 (IO3_38); also elsewhere on the board
D7B: FPGA.50 (IO3_50); also elsewhere on the board
D7C: FPGA.60 (IO3_60); also elsewhere on the board
D7D: FPGA.75 (IO5_75); also elsewhere on the board
DMINUS: U340G.6 (D-), USB1.2 (D-)
DPLUS: U340G.5 (D+), USB1.3 (D+)
E_21_B0: IOEXPAND_0X21_TOP.1 (GPB0); also elsewhere on the board
E_21_B1: IOEXPAND_0X21_TOP.2 (GPB1); also elsewhere on the board
E_21_B2: IOEXPAND_0X21_TOP.3 (GPB2); also elsewhere on the board
E_21_B3: IOEXPAND_0X21_TOP.4 (GPB3); also elsewhere on the board
E_21_B4: IOEXPAND_0X21_TOP.5 (GPB4); also elsewhere on the board
E_21_B5: IOEXPAND_0X21_TOP.6 (GPB5); also elsewhere on the board
E_21_B6: IOEXPAND_0X21_TOP.7 (GPB6); also elsewhere on the board
E_21_B7: IOEXPAND_0X21_TOP.8 (GPB7); also elsewhere on the board
E_ACSW1: IOEXPAND_0X20_BOT.1 (GPB0); also elsewhere on the board
E_ACSW2: IOEXPAND_0X20_BOT.2 (GPB1); also elsewhere on the board
E_ACSW3: IOEXPAND_0X20_BOT.3 (GPB2); also elsewhere on the board
E_ACSW4: IOEXPAND_0X20_BOT.4 (GPB3); also elsewhere on the board
E_GSW1: IOEXPAND_0X20_BOT.21 (GPA0); also elsewhere on the board
E_GSW2: IOEXPAND_0X20_BOT.22 (GPA1); also elsewhere on the board
E_GSW3: IOEXPAND_0X20_BOT.23 (GPA2); also elsewhere on the board
E_GSW4: IOEXPAND_0X20_BOT.24 (GPA3); also elsewhere on the board
E_IO_1: IOEXPAND_0X21_TOP.25 (GPA4), PIN_ANALOG_IOEXP.1
E_IO_2: IOEXPAND_0X21_TOP.26 (GPA5), PIN_ANALOG_IOEXP.3
E_IO_3: IOEXPAND_0X21_TOP.27 (GPA6), PIN_ANALOG_IOEXP.5
E_IO_4: IOEXPAND_0X21_TOP.28 (GPA7), PIN_ANALOG_IOEXP.7
E_OVSAMP1: IOEXPAND_0X20_BOT.25 (GPA4); also elsewhere on the board
E_OVSAMP2: IOEXPAND_0X20_BOT.26 (GPA5); also elsewhere on the board
E_SHDN1: IOEXPAND_0X20_BOT.5 (GPB4); also elsewhere on the board
E_SHDN2: IOEXPAND_0X20_BOT.6 (GPB5); also elsewhere on the board
GND: CG13.2, CG14.2, CG15.2, CV11.2, CV12.2, C_OSC.2, C_OSC1.2, C_OSC2.2, FPGA.4 (REFGND), FPGA.5 (ADC_VREF), FPGA.42 (GND5), FPGA.53 (GND4), FPGA.63 (GND12), FPGA.68 (GND3), FPGA.83 (GND2), FPGA.95 (GND1), FPGA.104 (GND11), FPGA.116 (GND10), FPGA.125 (GND9), FPGA.133 (GND8), FPGA.137 (GND7), FPGA.142 (GND6), FPGA.E (GND_PAD), IOEXPAND_0X20_BOT.10 (VSS), IOEXPAND_0X20_BOT.15 (A0), IOEXPAND_0X20_BOT.16 (A1), IOEXPAND_0X20_BOT.17 (A2), IOEXPAND_0X21_TOP.10 (VSS), IOEXPAND_0X21_TOP.16 (A1), IOEXPAND_0X21_TOP.17 (A2), JP1.6, JP1.10, OSC.2 (GND), PIN_AIN_IO2_PWRGND.1, PIN_AIN_IO2_PWRGND.6, PIN_AIN_IO2_PWRGND.8, PIN_AIN_IO2_PWRGND.10, PIN_AIN_IO2_PWRGND.12, PIN_AIN_IO2_PWRGND.14, PIN_AIN_IO2_PWRGND.16, PIN_ANALOG_IOEXP.9, PIN_ANALOG_IOEXP1.15, PIN_ANALOG_IOEXP1.16, PIN_DISPLAY.1, PIN_IO_1.1, RJ2.2, RLED1.2, RLED2.2, RLED3.2, RLED4.2, RS6.1, SW_RESET.P$2, U340G.1 (GND), USB1.5 (GND); also elsewhere on the board
IO_100: FPGA.100 (IO6_100), PIN_AIN_IO2_PWRGND.13
IO_101: FPGA.101 (IO6_101), PIN_AIN_IO2_PWRGND.15
IO_105: FPGA.105 (IO6_105), PIN_IO_1.9
IO_110: FPGA.110 (IO7_110), PIN_IO_1.3
IO_111: FPGA.111 (IO7_111), PIN_IO_1.4
IO_113: FPGA.113 (IO7_113), PIN_IO_1.5
IO_114: FPGA.114 (IO7_114), PIN_IO_1.6
IO_118: FPGA.118 (IO7_118), PIN_IO_1.7
IO_119: FPGA.119 (IO7_119), PIN_IO_1.8
IO_122: FPGA.122 (IO8_122), PIN_IO_1.10
IO_CLK_88: FPGA.88 (CLK2P), PIN_AIN_IO2_PWRGND.5
IO_CLK_89: FPGA.89 (CLK2N), PIN_AIN_IO2_PWRGND.7
IO_CLK_90: FPGA.90 (CLK3P), PIN_AIN_IO2_PWRGND.9
IO_CLK_91: FPGA.91 (CLK3N), PIN_AIN_IO2_PWRGND.11
JTAGEN: FPGA.15 (JTAGEN), JP1.7, RJ5.2
L21_SDA: FPGA.21 (IO1B_21), IOEXPAND_0X20_BOT.13 (SDA), IOEXPAND_0X21_TOP.13 (SDA), PIN_ANALOG_IOEXP.13, R_SDA.1; also elsewhere on the board
L120_SYNC: FPGA.120 (IO8_120); also elsewhere on the board
L121: FPGA.121 (IO8_121), PIN_AIN_IO2_PWRGND.4
L124: FPGA.124 (IO8_124), PIN_DISPLAY.10
L127: FPGA.127 (IO8_127), PIN_DISPLAY.9
L130: FPGA.130 (IO8_130), PIN_DISPLAY.8
L131: FPGA.131 (IO8_131), PIN_DISPLAY.6
L132: FPGA.132 (IO8_132), PIN_DISPLAY.7
L134: FPGA.134 (IO8_134), PIN_DISPLAY.5
L135: FPGA.135 (IO8_135), PIN_DISPLAY.4
L140: FPGA.140 (IO8_140), PIN_DISPLAY.3
L141_SCL: FPGA.141 (IO8_141), IOEXPAND_0X20_BOT.12 (SCL), IOEXPAND_0X21_TOP.12 (SCL), PIN_ANALOG_IOEXP.11, R_SCL.1; also elsewhere on the board
LED1: IOEXPAND_0X21_TOP.21 (GPA0), LED1.A
LED2: IOEXPAND_0X21_TOP.22 (GPA1), LED2.A
LED3: IOEXPAND_0X21_TOP.23 (GPA2), LED3.A
LED4: IOEXPAND_0X21_TOP.24 (GPA3), LED4.A
LOW_22: FPGA.22 (IO1B_22); also elsewhere on the board
LOW_24: FPGA.24 (IO1B_24); also elsewhere on the board
LOW_25: FPGA.25 (IO1B_25); also elsewhere on the board
unnamed: LED4.C, RLED4.1
unnamed: LED3.C, RLED3.1
unnamed: LED2.C, RLED2.1
unnamed: LED1.C, RLED1.1
unnamed: C_OSC1.1, U340G.7 (XI), Y1.1
unnamed: C_OSC2.1, U340G.8 (XO), Y1.2
NCONF: FPGA.129 (NCONFIG), RS9.2, SW_RESET.P$4
OSC1: FPGA.27 (CLK0P), OSC.3 (OUT)
SERIALFROMLEFT_98: FPGA.98 (IO6_98), PIN_ANALOG_IOEXP1.14
SERIALFROMRIGHT_TX_93: FPGA.93 (IO6_93), PIN_ANALOG_IOEXP1.11, U340G.2 (TX)
SERIALTOLEFT_96: FPGA.96 (IO6_96), PIN_ANALOG_IOEXP1.12
SERIALTORIGHT_RX_92: FPGA.92 (IO6_92), PIN_ANALOG_IOEXP1.13, U340G.3 (RX)
SLD: USB1.S1 (SLD), USB1.S2 (SLD), USB1.S3 (SLD), USB1.S4 (SLD)
SPARELEFT_102: FPGA.102 (IO6_102), PIN_ANALOG_IOEXP1.4
SPARERIGHT_99: FPGA.99 (IO6_99), PIN_ANALOG_IOEXP1.3
STATUS: FPGA.136 (NSTATUS), RS8.2
TCK: FPGA.18 (TCK), JP1.1, RJ2.1
TDI: FPGA.19 (TDI), JP1.5, RJ4.2
TDO: FPGA.20 (TDO), JP1.2
TMS: FPGA.16 (TMS), JP1.3, RJ3.2
TRIGINFROMLEFT_28: FPGA.28 (CLK1N), PIN_ANALOG_IOEXP1.8
TRIGINFROMRIGHT_86: FPGA.86 (IO5_86), PIN_ANALOG_IOEXP1.9
TRIGOUTORIGHT_87: FPGA.87 (IO5_87), PIN_ANALOG_IOEXP1.7
TRIGOUTTOLEFT_106: FPGA.106 (IO6_106), PIN_ANALOG_IOEXP1.10

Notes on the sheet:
LOW Speed
FPGA
Back pinout 2
Front pinout
Oscillator
Top pinouts
IO expanders
Serial to USB interface
LEDs
JTAG interface
Can take 5V from either the right side connector or the USB connector
Chip that talks UART over USB
Back pinout 1

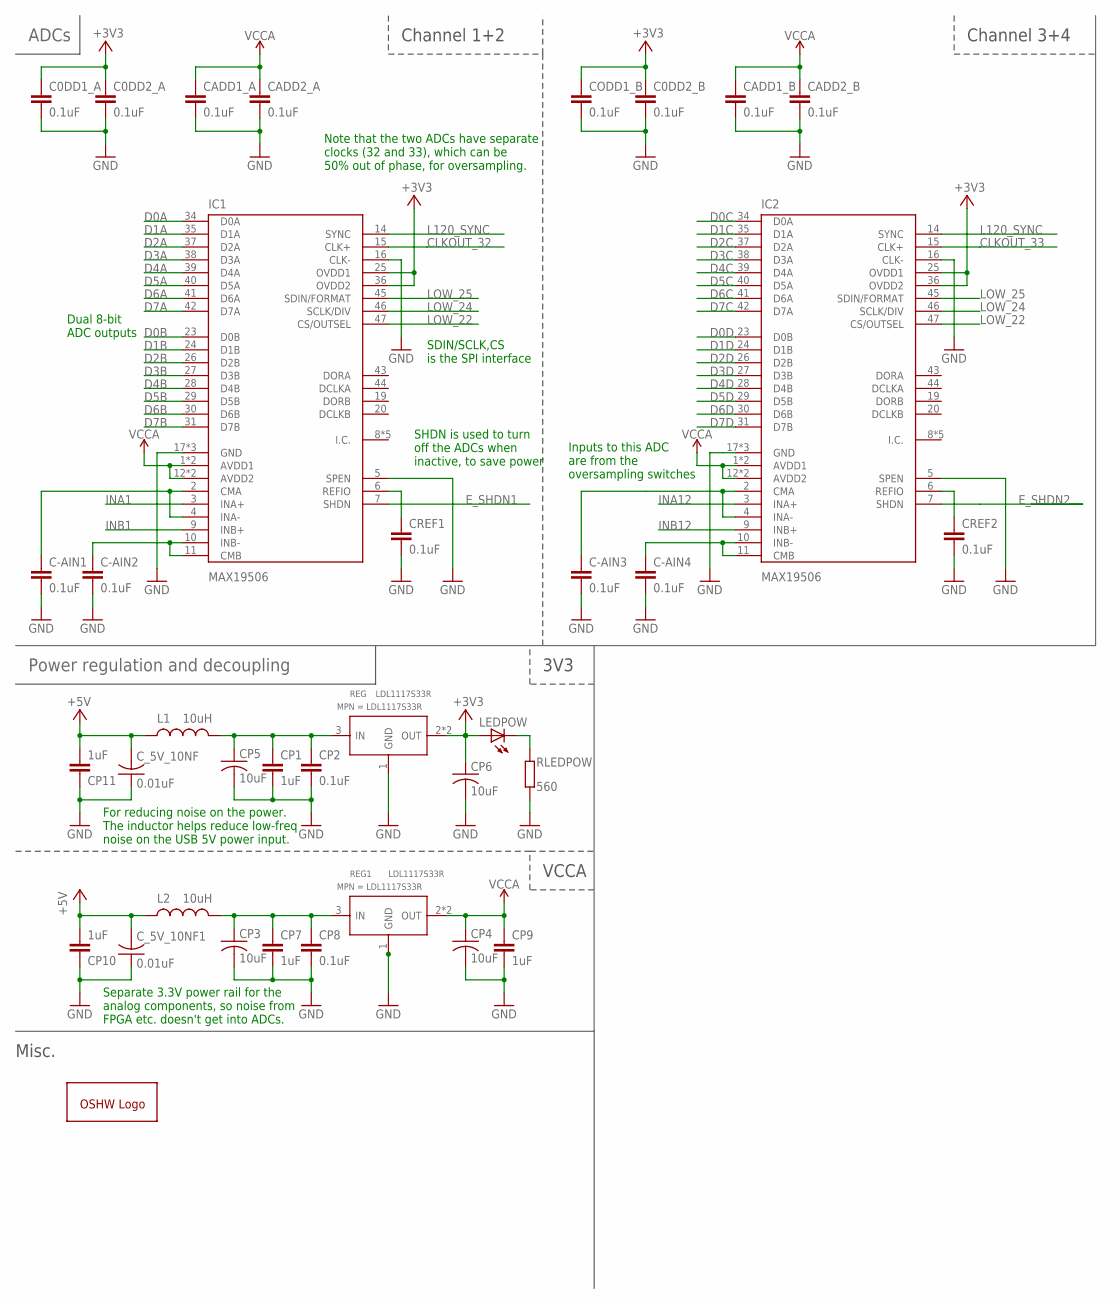
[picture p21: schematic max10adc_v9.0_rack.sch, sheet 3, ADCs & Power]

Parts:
C0DD1_A, C0DD2_A, C0DD2_B: 0.1uF; C0805K; MPN MF-CAP-0805-0.1uF
C-AIN1, C-AIN2, C-AIN3, C-AIN4: 0.1uF; C0805K; MPN MF-CAP-0805-0.1uF
CADD1_A, CADD1_B, CADD2_A, CADD2_B: 0.1uF; C0805K; MPN MF-CAP-0805-0.1uF
CODD1_B: 0.1uF; C0805K; MPN MF-CAP-0805-0.1uF
CP1, CP7, CP9, CP10, CP11: 1uF; C0805K; MPN MF-CAP-0805-1uF
CP2, CP8: 0.1uF; C0805K; MPN MF-CAP-0805-0.1uF
CP3, CP4, CP5, CP6: 10uF; C1206; MPN MF-CAP-1206-10uF
CREF1, CREF2: 0.1uF; C0805K; MPN MF-CAP-0805-0.1uF
C_5V_10NF, C_5V_10NF1: 0.01uF; C0603
GOLD_ORB_SM1: OSHWLOGOLOGO8MM; OSHW_8MM
IC1, IC2: MAX19506; TQFP-48; MPN MAX19506ETM+
L1, L2: 10uH; 1210; MPN MF-IND-1210-10uH
LEDPOW: MF-LED-0805-RED; SML0805; MPN MF-LED-0805-RED
REG, REG1: LDL1117S33R; SOT-223; MPN LDL1117S33R
RLEDPOW: 560; R0805; MPN MF-RES-0805-560

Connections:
+3V3: C0DD1_A.1, C0DD2_A.1, C0DD2_B.1, CODD1_B.1, CP6.1, IC1.25 (OVDD1), IC1.36 (OVDD2), IC2.25 (OVDD1), IC2.36 (OVDD2), LEDPOW.A, REG.2 (OUT), REG.TER (OUT); also elsewhere on the board
+5V: CP10.2, CP11.2, C_5V_10NF.2, C_5V_10NF1.2, L1.1, L2.1; also elsewhere on the board
CLKOUT_32: IC1.15 (CLK+); also elsewhere on the board
CLKOUT_33: IC2.15 (CLK+); also elsewhere on the board
D0A: IC1.34 (D0A); also elsewhere on the board
D0B: IC1.23 (D0B); also elsewhere on the board
D0C: IC2.34 (D0A); also elsewhere on the board
D0D: IC2.23 (D0B); also elsewhere on the board
D1A: IC1.35 (D1A); also elsewhere on the board
D1B: IC1.24 (D1B); also elsewhere on the board
D1C: IC2.35 (D1A); also elsewhere on the board
D1D: IC2.24 (D1B); also elsewhere on the board
D2A: IC1.37 (D2A); also elsewhere on the board
D2B: IC1.26 (D2B); also elsewhere on the board
D2C: IC2.37 (D2A); also elsewhere on the board
D2D: IC2.26 (D2B); also elsewhere on the board
D3A: IC1.38 (D3A); also elsewhere on the board
D3B: IC1.27 (D3B); also elsewhere on the board
D3C: IC2.38 (D3A); also elsewhere on the board
D3D: IC2.27 (D3B); also elsewhere on the board
D4A: IC1.39 (D4A); also elsewhere on the board
D4B: IC1.28 (D4B); also elsewhere on the board
D4C: IC2.39 (D4A); also elsewhere on the board
D4D: IC2.28 (D4B); also elsewhere on the board
D5A: IC1.40 (D5A); also elsewhere on the board
D5B: IC1.29 (D5B); also elsewhere on the board
D5C: IC2.40 (D5A); also elsewhere on the board
D5D: IC2.29 (D5B); also elsewhere on the board
D6A: IC1.41 (D6A); also elsewhere on the board
D6B: IC1.30 (D6B); also elsewhere on the board
D6C: IC2.41 (D6A); also elsewhere on the board
D6D: IC2.30 (D6B); also elsewhere on the board
D7A: IC1.42 (D7A); also elsewhere on the board
D7B: IC1.31 (D7B); also elsewhere on the board
D7C: IC2.42 (D7A); also elsewhere on the board
D7D: IC2.31 (D7B); also elsewhere on the board
E_SHDN1: IC1.7 (SHDN); also elsewhere on the board
E_SHDN2: IC2.7 (SHDN); also elsewhere on the board
GND: C0DD1_A.2, C0DD2_A.2, C0DD2_B.2, C-AIN1.2, C-AIN2.2, C-AIN3.2, C-AIN4.2, CADD1_A.2, CADD1_B.2, CADD2_A.2, CADD2_B.2, CODD1_B.2, CP1.2, CP2.2, CP3.2, CP4.2, CP5.2, CP6.2, CP7.2, CP8.2, CP9.2, CP10.1, CP11.1, CREF1.2, CREF2.2, C_5V_10NF.1, C_5V_10NF1.1, IC1.5 (SPEN), IC1.16 (CLK-), IC1.17 (GND), IC1.18 (GND), IC1.EP_GND (GND), IC2.5 (SPEN), IC2.16 (CLK-), IC2.17 (GND), IC2.18 (GND), IC2.EP_GND (GND), REG.1 (GND), REG1.1 (GND), RLEDPOW.2; also elsewhere on the board
INA1: IC1.3 (INA+); also elsewhere on the board
INA12: IC2.3 (INA+); also elsewhere on the board
INA-1: C-AIN1.1, IC1.2 (CMA), IC1.4 (INA-)
INA-2: C-AIN3.1, IC2.2 (CMA), IC2.4 (INA-)
INB1: IC1.9 (INB+); also elsewhere on the board
INB12: IC2.9 (INB+); also elsewhere on the board
INB-1: C-AIN2.1, IC1.10 (INB-), IC1.11 (CMB)
INB-2: C-AIN4.1, IC2.10 (INB-), IC2.11 (CMB)
L120_SYNC: IC1.14 (SYNC), IC2.14 (SYNC); also elsewhere on the board
LOW_22: IC1.47 (CS/OUTSEL), IC2.47 (CS/OUTSEL); also elsewhere on the board
LOW_24: IC1.46 (SCLK/DIV), IC2.46 (SCLK/DIV); also elsewhere on the board
LOW_25: IC1.45 (SDIN/FORMAT), IC2.45 (SDIN/FORMAT); also elsewhere on the board
unnamed: LEDPOW.C, RLEDPOW.1
unnamed: CP3.1, CP7.1, CP8.1, L2.2, REG1.3 (IN)
unnamed: CP1.1, CP2.1, CP5.1, L1.2, REG.3 (IN)
REF1: CREF1.1, IC1.6 (REFIO)
REF2: CREF2.1, IC2.6 (REFIO)
VCCA: CADD1_A.1, CADD1_B.1, CADD2_A.1, CADD2_B.1, CP4.1, CP9.1, IC1.1 (AVDD1), IC1.12 (AVDD2), IC1.13 (AVDD2), IC1.48 (AVDD1), IC2.1 (AVDD1), IC2.12 (AVDD2), IC2.13 (AVDD2), IC2.48 (AVDD1), REG1.2 (OUT), REG1.TER (OUT); also elsewhere on the board

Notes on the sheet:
ADCs
Power regulation and decoupling
3V3
VCCA
Channel 1+2
Channel 3+4
Misc.
Note that the two ADCs have separate clocks (32 and 33), which can be 50% out of phase, for oversampling.
SHDN is used to turn off the ADCs when inactive, to save power
SDIN/SCLK,CS is the SPI interface
Dual 8-bit ADC outputs
Inputs to this ADC are from the oversampling switches
For reducing noise on the power. The inductor helps reduce low-freq noise on the USB 5V power input.
Separate 3.3V power rail for the analog components, so noise from FPGA etc. doesn't get into ADCs.

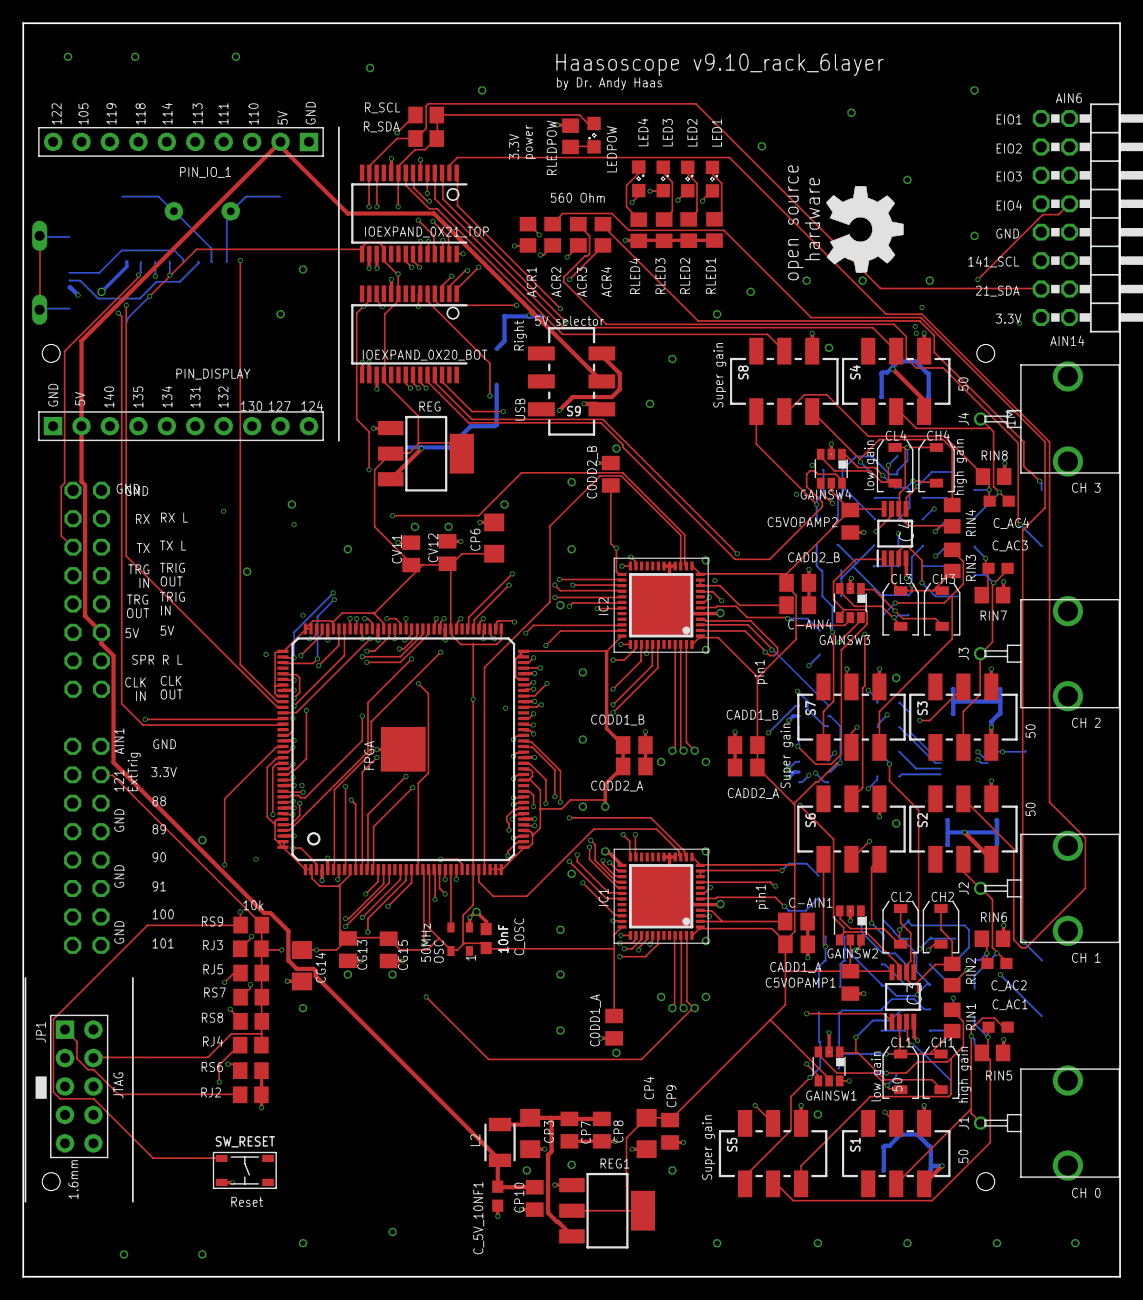
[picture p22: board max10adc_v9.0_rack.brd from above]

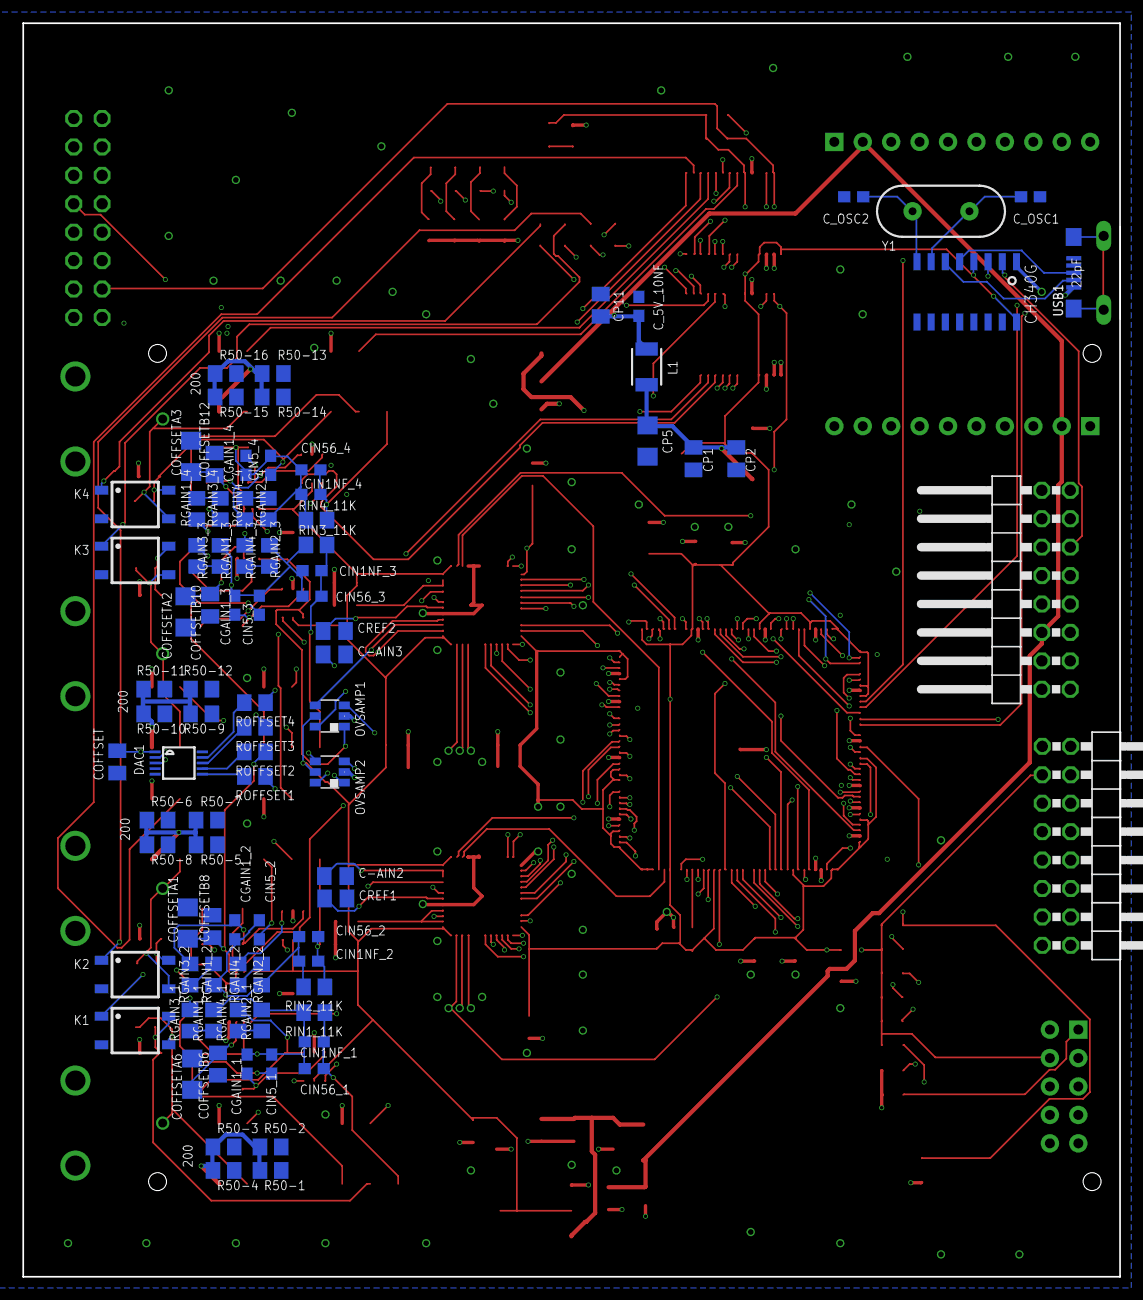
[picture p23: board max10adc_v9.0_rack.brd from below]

Board: 6 copper layers, 98.0 x 112.0 mm, 193 parts (89 on the bottom side), 204 nets.

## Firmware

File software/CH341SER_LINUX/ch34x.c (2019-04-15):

// 2013.7
//********************************************
//**  Copyright  (C)  WCH  2002-2013    ******
//**  Web:  http://www.winchiphead.com  ******
//********************************************
//**  Driver for USB to serial adaptor CH34X**
//**  GCC                                   **
//********************************************

// Support linux kernel version 2.6.25 and later
//

#include <linux/version.h>
#ifndef KERNEL_VERSION
#define	KERNEL_VERSION(ver, rel, seq)	((ver << 16) | (rel << 8) | (seq))
#endif

#include <linux/kernel.h>
#include <linux/errno.h>
#include <linux/init.h>
#include <linux/slab.h>
#include <linux/tty.h>
#include <linux/tty_driver.h>
#include <linux/tty_flip.h>
#include <linux/serial.h>
#include <linux/module.h>
#include <linux/moduleparam.h>
#include <linux/spinlock.h>
#include <asm/uaccess.h>
//#include <linux/uaccess.h>
#include <linux/usb.h>
#include <linux/usb/serial.h>

#define DRIVER_DESC		"WCH CH34x USB to serial adaptor driver"
#define DRIVER_AUTHOR	"<tech@wch.cn>"

#define CH34x_VENDOR_ID		0x1A86
#define CH340_PRODUCT_ID	0x7523
#define CH341_PRODUCT_ID	0x5523

#define CH34x_CLOSING_WAIT	(30 * HZ)

#define CH34x_BUF_SIZE		1024
#define CH34x_TMP_BUF_SIZE	1024

//Vendor define
#define VENDOR_WRITE_TYPE		0x40
#define VENDOR_READ_TYPE		0xC0

#define VENDOR_READ				0x95
#define VENDOR_WRITE			0x9A
#define VENDOR_SERIAL_INIT		0xA1
#define VENDOR_MODEM_OUT		0xA4
#define VENDOR_VERSION			0x5F

//For CMD 0xA4
#define UART_CTS		0x01
#define UART_DSR		0x02
#define UART_RING		0x04
#define UART_DCD		0x08
#define CONTROL_OUT		0x10
#define CONTROL_DTR		0x20
#define	CONTROL_RTS		0x40

//Uart state
#define UART_STATE			0x00
#define UART_OVERRUN_ERROR	0x01
#define UART_BREAK_ERROR	//no define
#define UART_PARITY_ERROR	0x02
#define UART_FRAME_ERROR	0x06
#define UART_RECV_ERROR		0x02
#define UART_STATE_TRANSIENT_MASK	0x07

//Port state
#define PORTA_STATE		0x01
#define PORTB_STATE		0x02
#define PORTC_STATE		0x03

//CH34x Baud Rate
#define CH34x_BAUDRATE_FACTOR	1532620800
#define CH34x_BAUDRATE_DIVMAX	3

#define DEBUG_CH34x
#undef  DEBUG_CH34x

#ifdef DEBUG_CH34x
#define dbg_ch34x( format, arg... )		\
	printk( KERN_DEBUG "%d: " format "\n", __LINE__, ##arg )
#else
#define dbg_ch34x( format, arg... )		\
do{									\
	if(0)							\
		printk(KERN_DEBUG "%d: " format "\n", __LINE__, ##arg);	\
} while (0)
#endif

#ifdef DEBUG_CH34x
#define err_ch34x( format, arg... )		\
	printk(KERN_ERR KBUILD_MODNAME ": " format "\n", ##arg)
#else
#define err_ch34x( format, arg... )   \
do{								\
	if(0)						\
	printk( KERN_ERR KBUILD_MODNAME ": " format "\n", ##arg)\
}while(0)						
#endif

// For debug
#if (LINUX_VERSION_CODE < KERNEL_VERSION(3,7,1))
static int debug = 1;
#endif

struct ch34x_buf {
	unsigned int buf_size;
	char *buf_buf;
	char *buf_get;
	char *buf_put;
};

struct ch34x_private {
	spinlock_t	lock;	//access lock
	struct ch34x_buf	*buf;
	int	write_urb_in_use;
	unsigned baud_rate;
	wait_queue_head_t	delta_msr_wait;
	u8	line_control;
	u8	line_status;
	u8	termios_initialized;
};

static struct usb_device_id	id_table [] = {
	{ USB_DEVICE(CH34x_VENDOR_ID, CH340_PRODUCT_ID) },
	{ USB_DEVICE(CH34x_VENDOR_ID, CH341_PRODUCT_ID) },
	{ } //End
};
MODULE_DEVICE_TABLE( usb, id_table );

#if (LINUX_VERSION_CODE < KERNEL_VERSION(3,5,2))
static struct usb_driver ch34x_driver = {
	.name		   = "ch34x",
	.probe		   = usb_serial_probe,
	.disconnect	   = usb_serial_disconnect,
	.id_table	   = id_table,
	.suspend	   = usb_serial_suspend,
	.resume		   = usb_serial_resume,
	.no_dynamic_id = 1,
	.supports_autosuspend = 1,
};
#endif

// ch34x_buf_alloc
// Allocate a circular buffer and all associated memory
static struct ch34x_buf *ch34x_buf_alloc( unsigned int size )
{
	struct ch34x_buf *pb;

	if( size == 0 )
		return NULL;

	pb = kmalloc( sizeof(struct ch34x_buf), GFP_KERNEL );
	if( pb == NULL )
		return NULL;

	pb->buf_buf = kmalloc( size, GFP_KERNEL );
	if( pb->buf_buf == NULL ) {
		kfree(pb);
		return NULL;
	}

	pb->buf_size = size;
	pb->buf_get = pb->buf_put = pb->buf_buf;

	return pb;
}

// ch34x_buf_free
// Free the buffer and all associated memory
static void ch34x_buf_free( struct ch34x_buf *pb )
{
	if( pb ) {
		kfree( pb->buf_buf );
		kfree( pb );
	}
}

// ch34x_buf_clear
// Clear out all data in the circular buffer
static void ch34x_buf_clear( struct ch34x_buf *pb )
{
	if( pb != NULL ) 
		pb->buf_get = pb->buf_put;
	// equivalent to a get of all data available
}

// ch34x_buf_data_avail
// Return the number of bytes of data available in he circular buffer
static unsigned int ch34x_buf_data_avail( struct ch34x_buf *pb )
{
	if( pb == NULL )
		return 0;

	return ((pb->buf_size + pb->buf_put - pb->buf_get) % pb->buf_size );
}

// ch34x_buf_space_avail
// Return the number of bytes of space available in the circular
static unsigned int ch34x_buf_space_avail( struct ch34x_buf *pb )
{
	if( pb == NULL )
		return 0;

	return ((pb->buf_size + pb->buf_get - pb->buf_put - 1) % pb->buf_size );
}

// ch34x_buf_put
// Copy data from a user buffer and put it into the circular buffer.
// Restrict to the amount of space available
// Return the number of bytes copied
static unsigned int ch34x_buf_put( struct ch34x_buf *pb,
		const char *buf, unsigned int count )
{
	unsigned int len;

	if( pb == NULL )
		return 0;

	len = ch34x_buf_space_avail(pb);
	if( count > len )
		count = len;
	else if( count == 0 )
		return 0;

	len = pb->buf_buf + pb->buf_size - pb->buf_put;
	if( count > len ) {
		memcpy( pb->buf_put, buf, len );
		memcpy( pb->buf_buf, buf+len, count - len );
		pb->buf_put = pb->buf_buf + count - len;
	}
	else {
		memcpy( pb->buf_put, buf, count );
		if( count < len )
			pb->buf_put += count;
		else if( count == len )
			pb->buf_put = pb->buf_buf;
	}

	return count;
}

static unsigned int ch34x_buf_get( struct ch34x_buf *pb,
		char *buf, unsigned int count )
{
	unsigned int len;

	if( pb == NULL )
		return 0;

	len = ch34x_buf_data_avail(pb);
	if( count > len )
		count = len;
	else if( count == 0 )
		return 0;

	len = pb->buf_buf + pb->buf_size - pb->buf_get;
	if( count > len ) {
		memcpy( buf, pb->buf_get, len );
		memcpy( buf+len, pb->buf_buf, count - len );
		pb->buf_get = pb->buf_buf + count - len;
	}
	else {
		memcpy( buf, pb->buf_get, count );
		if( count < len )
			pb->buf_get += count;
		else if( count == len )
			pb->buf_get = pb->buf_buf;
	}

	return count;
}

static int ch34x_vendor_read( __u8 request,
		__u16 value,
		__u16 index,
		struct usb_serial *serial,
		unsigned char *buf,
		__u16 len )
{
	int retval;

	retval = usb_control_msg( serial->dev, usb_rcvctrlpipe(serial->dev, 0), 
			request, VENDOR_READ_TYPE, value, index, buf, len, 1000 );
	dbg_ch34x("0x%x:0x%x:0x%x:0x%x %d - %d", 
			VENDOR_READ_TYPE, request, value, index, retval, len );

	return retval;
}

static int ch34x_vendor_write( __u8 request,
		__u16 value,
		__u16 index,
		struct usb_serial *serial,
		unsigned char *buf,
		__u16 len )
{
	int retval;

	retval = usb_control_msg( serial->dev, 
			usb_sndctrlpipe(serial->dev, 0),
			request,
			VENDOR_WRITE_TYPE,
			value, index, buf, len, 1000 );

	return retval;
}

static int set_control_lines( struct usb_serial *serial,
		u8 value )
{
	int retval;

	retval = ch34x_vendor_write( VENDOR_MODEM_OUT, (unsigned short)value, 
			0x0000, serial, NULL, 0x00 );
	dbg_ch34x("%s - value=%d, retval=%d", __func__, value, retval );

	return retval;
}

static int ch34x_get_baud_rate( unsigned int baud_rate,
		unsigned char *a, unsigned char *b )
{
	unsigned long factor = 0;
	short divisor = 0;

	if( !baud_rate )
		return -EINVAL;

	factor = (CH34x_BAUDRATE_FACTOR / baud_rate);
	divisor = CH34x_BAUDRATE_DIVMAX;

	while( (factor > 0xfff0) && divisor ) {
		factor >>= 3;
		divisor --;
	}

	if( factor > 0xfff0 )
		return -EINVAL;

	factor = 0x10000 - factor;
	*a = (factor & 0xff00) >> 8;
	*b = divisor;

	return 0;
}

#if (LINUX_VERSION_CODE >= KERNEL_VERSION(2,6,27))
static void ch34x_set_termios( struct tty_struct *tty,
		struct usb_serial_port *port, struct ktermios *old_termios )
{
#else
static void ch34x_set_termios( struct usb_serial_port *port,
		struct ktermios *old_termios )
{
	struct tty_struct *tty = port->tty;
#endif
	struct usb_serial *serial = port->serial;	
	struct ch34x_private *priv = usb_get_serial_port_data(port);
#if (LINUX_VERSION_CODE >= KERNEL_VERSION(3,7,1)) //sure
	struct ktermios *termios = &tty->termios;
#else
	struct ktermios *termios = tty->termios;
#endif
	unsigned int baud_rate;
	unsigned int cflag;
	unsigned long flags;
	u8 control;

	unsigned char divisor = 0;
	unsigned char reg_count = 0;
	unsigned char factor = 0;
	unsigned char reg_value = 0;
	unsigned short value = 0;
	unsigned short index = 0;
#if(LINUX_VERSION_CODE < KERNEL_VERSION(3, 10, 0))
	dbg_ch34x("%s - port:%d", __func__, port->number);
#else
	dbg_ch34x("%s - port:%d", __func__, port->port_number);
#endif
	
	spin_lock_irqsave( &priv->lock, flags );
	if( !priv->termios_initialized ) {
		*(termios) = tty_std_termios;
		termios->c_cflag = B9600 | CS8 | CREAD | HUPCL | CLOCAL;
		termios->c_ispeed = 9600;
		termios->c_ospeed = 9600;
		priv->termios_initialized = 1;
	}
	spin_unlock_irqrestore( &priv->lock, flags );

	/*
	 * The ch34x is reported to lose bytes if you change serial setting
	 * even to the same vaules as before. Thus we actually need to filter 
	 * in this specific case.
	 */
	if( !tty_termios_hw_change(termios, old_termios) )
		return;

	cflag = termios->c_cflag;
#if(LINUX_VERSION_CODE < KERNEL_VERSION(3, 10, 0))
	dbg_ch34x("%s (%d) cflag=0x%x\n", __func__, port->number, cflag);
#else
	dbg_ch34x("%s (%d) cflag=0x%x\n", __func__, port->port_number, cflag);
#endif
	// Get the byte size
	switch( cflag & CSIZE )
	{
		case CS5:
			reg_value |= 0x00;
			break;
		case CS6:
			reg_value |= 0x01;
			break;
		case CS7:
			reg_value |= 0x02;
			break;
		case CS8:
			reg_value |= 0x03;
			break;
		default:
			reg_value |= 0x03;
			break;
	}
	dbg_ch34x("%s - data bits = %d", __func__, reg_value + 0x05 );

	// Figure out the stop bits 
	if( cflag & CSTOPB ) {
		reg_value |= 0x04;
		dbg_ch34x("%s - stop bits = 2", __func__);
	}
	else 
		dbg_ch34x("%s - stop bits = 1", __func__);

	// Determine the parity
	if( cflag & PARENB )
		if( cflag & PARODD ) {
			reg_value |= (0x08 | 0x00);
			dbg_ch34x("%s - parity = odd", __func__);
		}
		else {
			reg_value |= (0x08 | 0x10);
			dbg_ch34x("%s - parity = even", __func__);
		}
	else
		dbg_ch34x("%s - parity = none", __func__);

	// Determine the baud rate
	baud_rate = tty_get_baud_rate( tty );
	dbg_ch34x("%s = baud_rate = %d", __func__, baud_rate);	
	ch34x_get_baud_rate( baud_rate, &factor, &divisor );	
	dbg_ch34x("----->>>> baud_rate = %d, factor:0x%x, divisor:0x%x",
				baud_rate, factor, divisor );	

	//enable SFR_UART RX and TX
	reg_value |= 0xc0;
	//enable SFR_UART Control register and timer
	reg_count |= 0x9c;

	value |= reg_count;
	value |= (unsigned short)reg_value << 8;
	index |= 0x80 | divisor;
	index |= (unsigned short)factor << 8;
	ch34x_vendor_write( VENDOR_SERIAL_INIT, value, index, serial, NULL, 0 );

	// change control lines if we are switching to or from B0
	spin_lock_irqsave( &priv->lock, flags ); 
	control = priv->line_control;
	if( (cflag & CBAUD) == B0 )
		priv->line_control &= ~(CONTROL_DTR | CONTROL_RTS);
	else
		priv->line_control |= (CONTROL_DTR | CONTROL_RTS);

	if( control != priv->line_control ) {
		control = priv->line_control;
		spin_unlock_irqrestore( &priv->lock, flags );
		set_control_lines( serial, control );
	}
	else
		spin_unlock_irqrestore( &priv->lock, flags );

	if( cflag & CRTSCTS )
		ch34x_vendor_write( VENDOR_WRITE, 0x2727, 0x0101, serial, NULL, 0);

	// FIXME: Need to read back resulting baud rate
	if( baud_rate )
		tty_encode_baud_rate(tty, baud_rate, baud_rate);

}
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

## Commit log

2017-12-05 move more stuff
    [max10adc.brd, max10adc.sch]
2017-12-05 some more stuff
    [max10adc.brd, max10adc.sch]
2017-12-05 routing of 8.6
    [max10adc.brd, max10adc.sch]
2017-12-06 for board 8
    [max10adc.brd, max10adc.sch]
2017-12-08 8.6 improvements
    [max10adc.brd, max10adc.sch]
2017-12-17 updates for v8.5 and v8.6
    [max10adc.brd, max10adc.sch]
2017-12-20 for 8.7 with separate VCCA
    [max10adc.brd, max10adc.sch]
2017-12-20 for 8.7 and USB2
    [max10adc.brd, max10adc.sch]
2017-12-20 for 8.7 use 1210 10uF caps for offset
    [max10adc.brd, max10adc.sch]
2017-12-20 for 8.7 fix some text etc
    [max10adc.brd]
2017-12-24 v8.7 just ordered from AllPCB
    [max10adc.brd, max10adc.sch]
2017-12-24 v8.8 with 50pF low gain caps
    [max10adc.brd, max10adc.sch]
2017-12-24 1nF+56pF -> 1nF
    [max10adc.brd]
2018-02-10 oshw logo
    [max10adc.brd, max10adc.sch]
2018-02-15 move USB to back of board
    [max10adc.brd]
2018-02-15 send i2c only to given board or all boards, and fix line width after selection
2018-02-15 go back to READ in case i2c is already busy
2018-02-16 v8.81, 196 ordered on macrofab, labeled all pins
    [max10adc.brd]
2018-02-22 fix 121 label
    [max10adc.brd]
2018-02-27 auto calibration
2018-03-16 usb serial debug printouts
2018-03-20 9 samples
2018-03-22 gerbers and BOM
    [max10adc.xls]
2018-04-03 auto calib
    [max10adc.xls]
2018-04-10 print in construct
2018-04-11 don't plot first sample, and deal with oversampling and deal with resampling... also force downsample to 0 when oversampling
2018-04-21 fix persist plot for 511 samples
2018-05-10 better color choices for single board running
2018-05-10 give up on dpdt for now
    [max10adc dpdt.brd, max10adc dpdt.sch]
2018-05-17 example of printing fft info
2018-05-18 don't import numpy by default, and cleanup phase diff printout
2018-05-20 mess with leds
2018-05-20 mess with leds more
2018-05-29 allow for 10M/1.1M/11k resistors
2018-06-09 print version name at startup
2018-06-11 v9, label left/right pins, switch pin 28
    [max10adc_v9.0.brd, max10adc_v9.0.sch]
2018-06-11 v9, with 10M, 1.1M, and 11k input resistors, and rerouted
    [max10adc_v9.0.brd, max10adc_v9.0.sch, max10adc_v9.xls]
2018-06-11 rotate osh logo
    [max10adc_v9.0.brd]
2018-06-11 populate more th parts
    [max10adc_v9.xls]
2018-10-02 cleanup schematic
    [max10adc_v9.0.sch]
2018-10-02 minor sch cleanup
    [max10adc_v9.0.sch]
2018-10-04 3 sch sheets
    [max10adc_v9.0.sch]
2018-10-09 updates for board 9.0 with dpdt switches
    [max10adc_v9.0.brd, max10adc_v9.0.sch]
2018-10-09 Cleanup schematic. Fit pages to A3. Replaces some SMD resistor so all resistor symbols are the same
    [max10adc_v9.0.brd, max10adc_v9.0.sch]
2018-10-09 Changed values from 200 to 200R
    [max10adc_v9.0.brd, max10adc_v9.0.sch]
2018-10-09 Fixed small visual error
    [max10adc_v9.0.sch]
2018-10-09 clean up a few things
    [max10adc_v9.0.brd, max10adc_v9.0.sch]
2018-10-09 add some notes to the schematics
    [max10adc_v9.0.sch]
2018-10-26 remove 4 leds
    [max10adc_v9.0.xls]
2018-10-29 acquire only samplestosend samples, and only signal data ready after all samples have been acquired
2018-11-01 update some parts to TTI
    [max10adc_v9.0.xls]
2018-11-19 for board v9.0
2018-11-26 remove v8 stuff
    [max10adc.brd, max10adc.sch, max10adc.xls]
2018-11-26 deal with multiple boards for reading switches, in theory
2018-11-26 set gain to 1.1 for v9.0 boards
2018-11-27 for 9.01
    [max10adc_v9.0.xls]
2018-11-27 for allpcb
    [max10adc_v9.0.xls]
2018-12-04 just 6miil distance between drills and traces
2018-12-04 better routing, using just 6mil distance between drills and traces
    [max10adc_v9.0.brd]
2018-12-04 150 Ohm inputs for v9.0 boards?
2018-12-04 150 Ohm inputs for all
2018-12-07 300 Ohm termination
2018-12-15 Update README.md
    I've created a 3D model for bottom case. It might come handy also for others.
2018-12-19 case for v8.81
    [Haasoscope_v8.81_case.stl]
2018-12-22 names on silkscreen
    [max10adc_v9.0.brd, max10adc_v9.0.sch]
2018-12-22 bottom labels
    [max10adc_v9.0.brd]
2019-01-03 v9.01 case and firmware
    [Haasoscope_v9.01_case.stl]
2019-01-10 deal with supergain and 50ohm detection for multiple boards
2019-01-28 fix crash in printout
2019-02-05 check for raspberry pi
2019-02-17 HW_INIT: Board id, firmware version. Same content, different structure of data
2019-03-21 for stacking
    [customizable-cylinder_18mm.stl, customizable-cylinder_25mm.stl]
2020-09-08 multi board bug fixes
2021-04-16 save data for other board channels too
2021-04-16 for connecting multiple v9 boards
2021-04-16 connecting case
    [Haasoscope_v9.01_case_connect.stl]
2021-04-22 150 ohm termination
2021-04-25 prepare to merge version9
    [max10adc_v8.brd, max10adc_v8.sch, max10adc_v8.xls]
2021-04-26 try to support more than 10 boards
2021-04-26 firmware 18, more than 10 boards
2021-04-26 supporting more than 10 boards, requiring firmware 17 or higher
2021-05-01 wait for normal triggers to stop before calibrating trigger bins
2021-05-03 only increment clock phase on selected board
2021-05-03 store all digital logic analyzer bits from all boards
2021-05-04 talk to trigger board over serial
2021-05-06 all boards send triggers out to the right when in noselftrig mode
2021-05-10 make sure we can talk to the trig board
2021-05-13 minor, and expect all boards to have a trigger cable connection
2021-05-19 few more speedups, now 500 Hz for r12 for b3
2021-05-19 handle negative y values, print MB/s
2021-05-20 3U rack compatible
    [max10adc_v9.0_rack.brd, max10adc_v9.0_rack.sch]
2021-05-21 3U rack backplane
    [rack_backplane_v9.0.brd, rack_backplane_v9.0.sch]
2021-05-21 before routing
    [max10adc_v9.0_rack.brd, rack_backplane_v9.0.brd, rack_backplane_v9.0.sch]
2021-05-21 ordered version of scope and backplane
    [max10adc_v9.0_rack.brd, rack_backplane_v9.0.brd, rack_backplane_v9.0.sch]
2021-05-23 trying to fix the glitch in the first sample of ch0, but no luck yet
2021-05-24 fixed the glitch in the first sample of ch0, and pass timing, though with a few set_false_paths
2021-05-26 working pretty well, but r12 is missing a sample, and first 2 points of ch0 are identical
2021-05-28 update IP
    [myadc.csv]
2021-06-02 better check for fastusb devices
2021-06-02 fix spacing of trigboard
    [rack_backplane_v9.0.brd]
2021-06-02 add 6mm on top and bottom, to fit in sliders
    [max10adc_v9.0_rack.brd]
2021-06-10 put usb serial on bottom clean up wire stubs
    [max10adc_v9.0_rack.brd]
2021-06-14 minor, less printouts, etc.
2021-06-14 update chunksize based on num samples
2021-06-14 run trig board at 921600 baud
2021-06-15 remove 2 wire stubs
    [max10adc_v9.0_rack.brd]
2021-06-15 use max 4416EUA, which is available
    [max10adc_v9.0_rack.brd, max10adc_v9.0_rack.sch]
2021-07-06 add gnd layer on layer 15
    [rack_backplane_v9.0.brd, rack_backplane_v9.0.sch]
2021-07-07 routed v9.10 6layer rack
    [max10adc_v9.0_rack.brd]
2021-09-30 save in float32, so time axis has enough precision (and voltage?)
2021-11-23 print error and exit if you try to do fastusb with old firmware
2022-03-03 get trigratecounter every 10s and print to chantext area allow cointime to also be "deadtime" for trigger rate counter
2022-05-26 trigger counter every 2s, printouts for rolling trigger
2022-12-28 don't draw old junk if there was a timeout getting data (as often the case with no rolling trigger)
2022-12-28 Make timedout True if any board times out
2023-03-24 trig out for ~80ns on pin 101 if noselftrig is false (the default)
2023-06-12 update trigger board with ext trig in, and add old one
    [haasoscope_trigger_board_v1.1.brd, haasoscope_trigger_board_v1.1.sch, haasoscope_triggerout_board.brd, haasoscope_triggerout_board.sch]
2024-05-24 can also control pin 12

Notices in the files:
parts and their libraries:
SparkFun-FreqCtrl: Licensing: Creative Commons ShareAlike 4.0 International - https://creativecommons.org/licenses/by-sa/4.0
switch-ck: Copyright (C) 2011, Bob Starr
